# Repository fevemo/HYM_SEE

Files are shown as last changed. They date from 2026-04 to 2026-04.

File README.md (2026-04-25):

# Hack your microscope 2026 challenge - Group See

This repository contains all of the resources developed by group See for the HYM 2 day challenge: Organoid sorting with microfluidics.

The code provides visualization of the image caputred by a Hikrobotics camera with simultaneous control of the poseidon syringe pump system. On top of the real-time image we compute a difference image with respect to a reference and then identify flowing particles based on a tunable threshold level. Once the mask is computed the size of the particles is estimated by counting the total masked pixels.

## List of materials

-  [Poseidon pump system](https://github.com/pachterlab/poseidon)
-  [OpenUC2 Corebox](https://openuc2.com/product-overview-2/)
-  [Hikrobotics MV-CS060-10UM-PRO](https://www.hikrobotics.com/en/machinevision/productdetail/?id=5715)
-  [3x 1ml BD plastic syringe](https://www.digikey.pt/short/93zf92hf)
-  [2m of Tygon tube ND-100-80 (ID: 0.04 in, OD: 0.07 in)](https://darwin-microfluidics.com/products/tygon-nd-100-80-micro-tubing)
-  [3 Tube Tuck Luer Connector for 1/16 tubing (1 pack)](https://www.microfluidic-chipshop.com/connectors/1243-2683-tube-tuck-mini-luer-connector-for-116-tubing-fluidic-158-html#/20-material-tpe/26-color-blue)
-  [Custom open UC2 adapter plate for the XY stage](https://github.com/fevemo/HYM_SEE/blob/main/adapter_base_puzzle_v3.stl)
-  XY stage with M6 holes.
-  3x M6 screws
-  Slide holder made with Thorlabs parts: post-holder, optical post and two CL5 parts to clamp the microfluidic chip, using an M6 screw.
-  Windows PC.

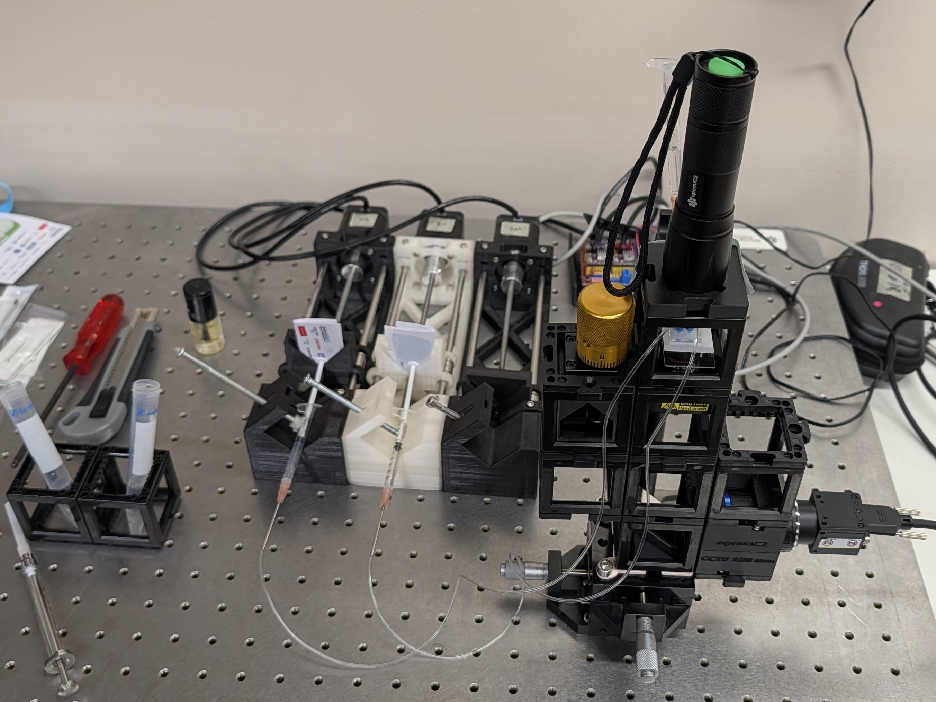
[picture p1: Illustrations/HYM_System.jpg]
HYM_System


## Optical setup
The microscope was build using the [OpenUC2 Corebox](https://openuc2.com/product-overview-2/). Documentation about the corebox can be found [here](https://docs.openuc2.com/usage/disc/corebox/en/core_intro/). The optical setup was adapted to be able to fit on a Melles Griot Stage for XY translation while fixing the sample with a Thorlabs post holder. An [adaptor](https://github.com/fevemo/HYM_SEE/blob/main/adapter_base_puzzle_v3.stl) was designed to fix the openUC2 microscope to the stage. 

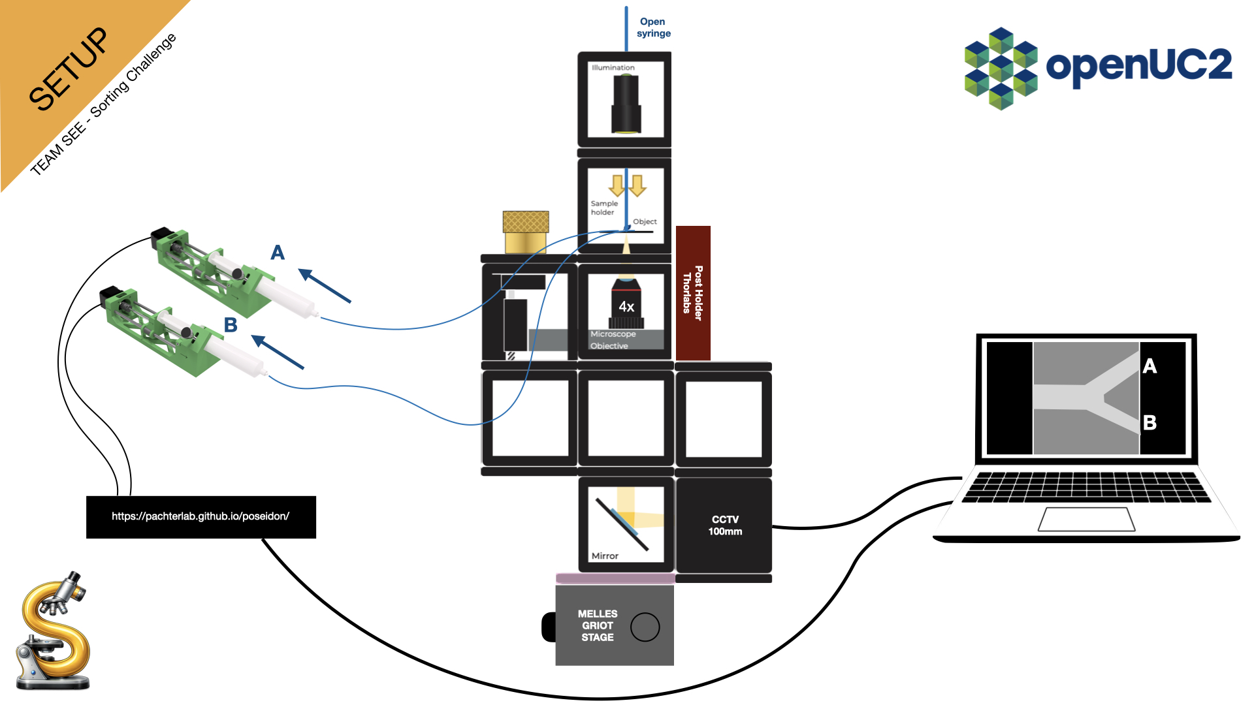
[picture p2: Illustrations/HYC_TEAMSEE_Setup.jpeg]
HYM_SEE_Setup


## Microfluidics design
The microfluidics [channel design](https://github.com/fevemo/HYM_SEE/blob/main/microfluidic-channel.stl) was lasercut into two layers of double sided tape, after which it was sticked on a glass microscopy slide. On top, a PMMA layer with in and outlets of 2.5mm (lasercut) was sticked on the top of the chip. ChipShop adaptors were inserted into the in and outlets to attach the tubing to the chip and connect them with the two syringe pumps. The inlet of the chip was connected with an open syringe in which the diluted particle sample can be loaded.

## Pump control
The Poseidon pumps were used in their original configuration and controled via serial commands from a custom python API. The API converts real-time control commands such as forward, back, stop, etc. into the command strings the Poseion arduino system expects. This was a great way to get up and running quickly but the serial comunication starts having issues as soon as several commands are sent in quick successsion. In the future it would be better to modify the pump controller to accomodate better real-time control.

## Camera control
The Hikrobot camera was controlled using the USB3 Vision protocol and using a custom API. Our API was built on an already existing API made available by Hikrobot (src/Python) and adapted for our specific use case. This API allows the connection to the camera, the start of acquisition, the change of exposure time, and the registering of a frame.

## Graphical User Interface
The GUI was made using napari as the main block. The camera and the syringe pumps were connected to the PC, and the communication was managed using Python. New frames were acquired in real time and used to update a napari layer, which enabled real-time visualization of the microfluidic chip. Some basic functions were implemented for camera control, such as the ability to change the exposure time of the camera and choose a folder in the PC for .tiff snap capture saving.

The ability to programmatically control the two syringe pumps was also implemented on the GUI, with speed control for each one and the ability to choose the pulling or pushing motion of the syringe, creating a forward or backward fluidic motion. Finally, a referencing button was also added, which could be used to create a subtraction image (subtraction_image = live - reference), which could be used for the segmentation of beads in the FOV.

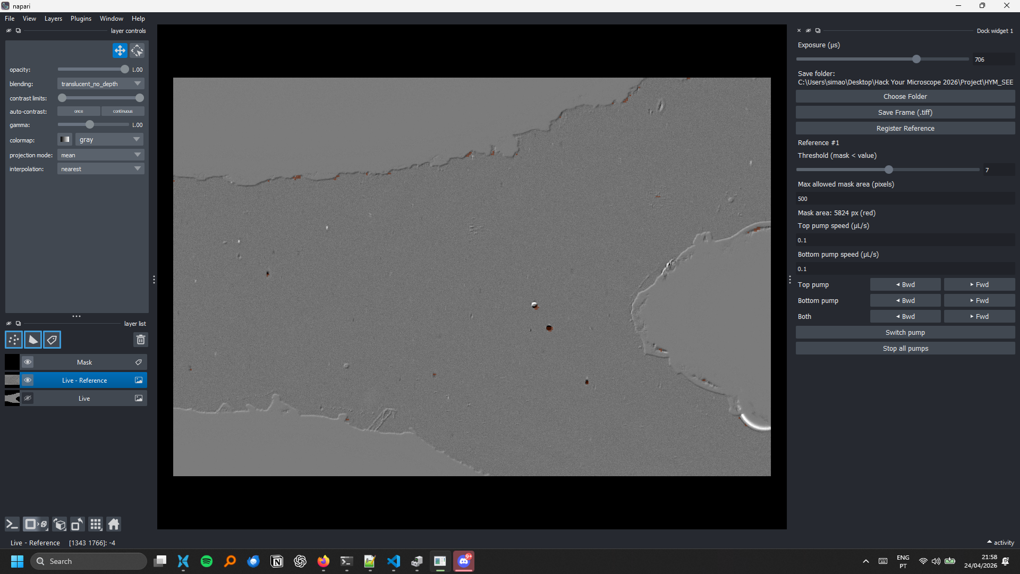
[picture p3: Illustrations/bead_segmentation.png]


## Setup

**macOS/Linux:**
```sh
./install.sh
source .venv/bin/activate
```

**Windows:**
```bat
install.bat
.venv\Scripts\activate
```

The install scripts will set up a Python 3.11 virtual environment and install all dependencies automatically.

**For camera control:**

Installation of the Hikrobotics MVS control software which includes the SDK installation.

## Run

Make sure the virtual environment is activated (see Setup above) before running. You need to do this each time you open a new terminal. Then run the desired code. 

```sh
python src/main_GUI.py
```

## Limitations / To-Dos:
1.	Software:
   
-	build on the already existing particle recognition and implement an automated feedback loop to the pumps to steer the particles to the correct outlet channel automatically.
  
2.	Hardware components:
 	
a.	Microfluidics:
-	Fine tuning of the pumps with adaptation of the pump’s response time for a more accurate sorting mechanism
-	Fine tuning of the microfluidic chamber width to optimise the response time to the pump system
-	The microfluid chip can be improved with a more optimised manufacturing process to achieve smoother edges.
-	a better inlet mechanism could be implemented to sort larger amounts of the sample.
  
b.	Optical Setup:
-	Implement a Fluorescence module for sorting based on spectral readout.

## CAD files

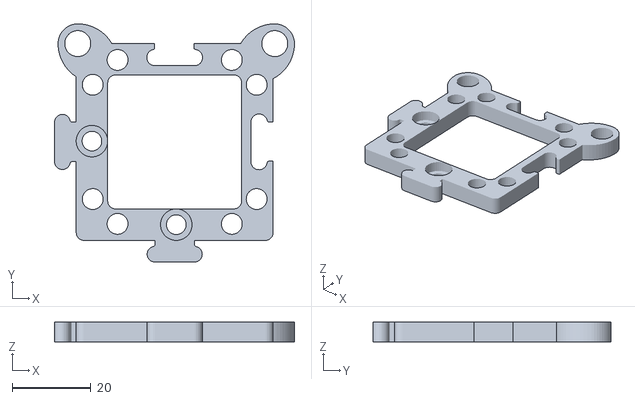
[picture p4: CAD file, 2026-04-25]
Hardware/adapter_base_puzzle_v3.stl
60.9 x 60.5 x 5.00

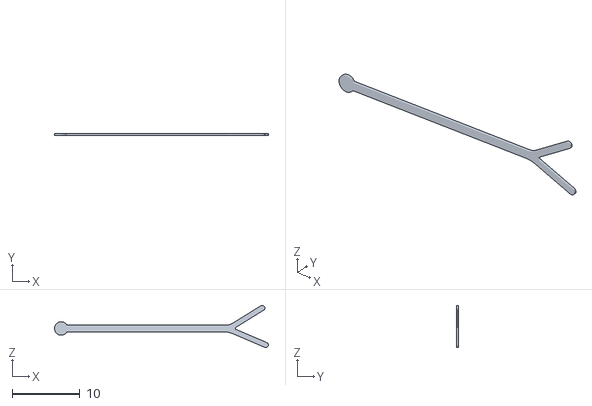
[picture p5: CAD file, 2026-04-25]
Hardware/microfluidic-channel.stl
31.6 x 0.3 x 6.24

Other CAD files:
Hardware/microfluidcs_channel_sketch.ipt

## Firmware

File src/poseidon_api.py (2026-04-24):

#!/usr/bin/env python3
"""
poseidon_api.py  -  Poseidon Pump serial API
=============================================

Two sending modes
-----------------
blocking=True  (default)
    Sends the command and waits for the Arduino's reply frame before returning.
    Use this for settings and for precise sequenced moves.

blocking=False  (fire-and-forget)
    Writes the bytes to the serial buffer and returns immediately without
    reading a reply.  Latency is essentially zero (just the USB write).
    Use this for start/stop automation where timing matters.

Quick start
-----------
    from poseidon_api import PoseidonController

    with PoseidonController("/dev/tty.usbmodem14101", microsteps=32) as pump:
        pump.set_speed(1, 1.0, "mL")
        pump.set_accel(1, 2.0, "mL")

        # ── fire-and-forget style (fast start / stop) ──
        pump.run_continuous(pumps=[1], direction="F", blocking=False)
        time.sleep(2.0)
        pump.stop(blocking=False)

        # ── blocking style (precise displacement) ──
        pump.move(1, 0.5, "mL", "F", blocking=True)
"""

import time
from threading import Lock
from typing import List, Optional

import serial
import serial.tools.list_ports

# ── Constants ─────────────────────────────────────────────────────────────────

BAUD_RATE = 230400

SYRINGE_OPTIONS = [
    "BD 1 mL", "BD 3 mL", "BD 5 mL",
    "BD 10 mL", "BD 20 mL", "BD 30 mL", "BD 60 mL",
]
SYRINGE_AREAS = [
    17.34206347, 57.88559215, 112.9089185,
    163.539454,  285.022957,  366.0961536, 554.0462538,
]  # mm² inner cross-section (BD plastic syringes)

# ── Conversion helpers ────────────────────────────────────────────────────────

def _mm2steps(mm: float, microsteps: int) -> float:
    """1 rev = 0.8 mm, 200 full steps/rev."""
    return mm / 0.8 * 200.0 * microsteps

def _to_steps(value: float, unit: str, area_mm2: float, microsteps: int) -> float:
    if unit == "mm":
        return _mm2steps(value, microsteps)
    if unit == "mL":
        return _mm2steps(value * 1000.0 / area_mm2, microsteps)
    if unit == "uL":
        return _mm2steps(value / area_mm2, microsteps)
    raise ValueError(f"Unknown unit '{unit}'. Use 'mm', 'mL', or 'µL'.")

# ── Serial low-level helpers ──────────────────────────────────────────────────

def _auto_port() -> Optional[str]:
    tokens = ["usbmodem", "usbserial", "wchusbserial", "ttyACM", "ttyUSB"]
    ports  = [p.device for p in serial.tools.list_ports.comports()]
    for tok in tokens:
        for p in ports:
            if tok.lower() in p.lower():
                return p
    return ports[0] if ports else None


def _read_frame(ser: serial.Serial, timeout_s: float = 2.0) -> Optional[str]:
    """Read one '<…>' reply frame from the Arduino."""
    deadline = time.time() + timeout_s
    while time.time() < deadline:
        b = ser.read(1)
        if b == b"<":
            break
    else:
        return None
    buf = bytearray()
    while time.time() < deadline:
        b = ser.read(1)
        if b == b">":
            return buf.decode("utf-8", errors="replace")
        buf.extend(b)
    return None


# ── Main API class ────────────────────────────────────────────────────────────

class PoseidonController:
    """
    Serial API for one Poseidon controller board (up to 3 pumps).

    Parameters
    ----------
    port        : Serial port string, or None to auto-detect.
    microsteps  : Microstepping level matching the physical driver jumper (1-32).
    syringe     : Syringe name from SYRINGE_OPTIONS (for mL/µL unit conversion).
    """

    def __init__(
        self,
        port: Optional[str] = None,
        microsteps: int = 32,
        syringe: str = "BD 1 mL",
    ):
        self._port       = port or _auto_port()
        self._microsteps = microsteps
        syringe_idx      = SYRINGE_OPTIONS.index(syringe)
        self._area       = SYRINGE_AREAS[syringe_idx]
        self._ser: Optional[serial.Serial] = None
        self._lock       = Lock()   # guards concurrent serial writes from threads

    # ── Context manager ───────────────────────────────────────────────────────

    def __enter__(self) -> "PoseidonController":
        self.connect()
        return self

    def __exit__(self, *_) -> None:
        self.disconnect()

    # ── Connection ────────────────────────────────────────────────────────────

    def connect(self) -> None:
        """Open the serial port and wait for the Arduino to boot."""
        print(f"[INFO] Connecting to {self._port} @ {BAUD_RATE} baud…")
        self._ser = serial.Serial(
            port=self._port, baudrate=BAUD_RATE, timeout=0.1
        )
        time.sleep(2.5)  # Arduino resets on serial open
        hello = _read_frame(self._ser, timeout_s=3.0)
        print(f"[INFO] Arduino: {hello or '(no greeting)'}")

    def disconnect(self) -> None:
        """Close the serial port."""
        if self._ser and self._ser.is_open:
            self._ser.close()
        self._ser = None
        print("[INFO] Disconnected.")

    @property
    def connected(self) -> bool:
        return self._ser is not None and self._ser.is_open

    # ── Raw send ──────────────────────────────────────────────────────────────

    def send_raw(self, cmd: str, blocking: bool = True) -> Optional[str]:
        """
        Send a raw '<…>' command string.

        Parameters
        ----------
        cmd      : Full command string including angle brackets.
        blocking : If True, wait for and return the Arduino reply frame.
                   If False, write and return immediately (fire-and-forget).

        Returns
        -------
        Reply string (blocking) or None (fire-and-forget / timeout).
        """
        if not self.connected:
            raise RuntimeError("Not connected. Call connect() first.")
        if not (cmd.startswith("<") and cmd.endswith(">")):
            raise ValueError(f"Command must be wrapped in <>: {cmd}")

        print(f"[TX] {cmd}")
        with self._lock:
            self._ser.write(cmd.encode("utf-8"))
            self._ser.flush()
            if not blocking:
                return None
            reply = _read_frame(self._ser, timeout_s=2.0)

        print(f"[RX] {reply or '(no reply)'}")
        return reply

    # ── Settings ──────────────────────────────────────────────────────────────

    def set_speed(self, pump: int, value: float, unit: str = "mm",
                  blocking: bool = True) -> Optional[str]:
        """Set speed for pump 1-3 in physical units per second."""
        steps = _to_steps(value, unit, self._area, self._microsteps)
        return self.send_raw(
            f"<SETTING,SPEED,{pump},{steps:.4f},F,0.0,0.0,0.0>", blocking
        )

    def set_accel(self, pump: int, value: float, unit: str = "mm",
                  blocking: bool = True) -> Optional[str]:
        """Set acceleration for pump 1-3 in physical units per second²."""
        steps = _to_steps(value, unit, self._area, self._microsteps)
        return self.send_raw(
            f"<SETTING,ACCEL,{pump},{steps:.4f},F,0.0,0.0,0.0>", blocking
        )

    # ── Motion: fixed displacement ────────────────────────────────────────────

    def move(self, pump: int, value: float, unit: str = "mm",
             direction: str = "F", blocking: bool = True) -> Optional[str]:
        """
        Move one pump by a fixed displacement and (optionally) wait for reply.

        The Arduino moves asynchronously once the command is received;
        'blocking' here only controls whether Python waits for the serial ACK,
        not for the motor to finish.
        """
        steps  = _to_steps(value, unit, self._area, self._microsteps)
        signed = steps if direction == "F" else -steps
        d      = [0.0, 0.0, 0.0]
        d[pump - 1] = signed
        return self.send_raw(
            f"<RUN,DIST,{pump},0.0,F,{d[0]},{d[1]},{d[2]}>", blocking
        )

    def move_all(self, values: List[float], unit: str = "mm",
                 direction: str = "F", blocking: bool = True) -> Optional[str]:
        """
        Move all 3 pumps simultaneously by given displacements.
        values = [v1, v2, v3]; use 0.0 to skip a pump.
        """
        d = [
            _to_steps(v, unit, self._area, self._microsteps)
            * (1 if direction == "F" else -1)
            for v in values
        ]
        return self.send_raw(
            f"<RUN,DIST,123,0.0,F,{d[0]},{d[1]},{d[2]}>", blocking
        )

    # ── Motion: continuous (run until stop) ───────────────────────────────────

    def run_continuous(
        self,
        pumps: List[int],
        direction: str = "F",
        blocking: bool = False,
    ) -> Optional[str]:
        """
        Start one or more pumps at their configured speed indefinitely.

        The firmware treats a distance of 999999 as "run until stopped",
        which is the same behaviour as the original RUN mode.

        Parameters
        ----------
        pumps     : List of pump IDs to run, e.g. [1], [1, 3], [1, 2, 3].
        direction : 'F' forward, 'B' backward.
        blocking  : False by default - returns immediately after writing
                    the command so you can time the stop precisely.
        """
        pump_str = "".join(str(p) for p in sorted(pumps))
        sign     = 1 if direction == "F" else -1
        dist     = sign * 999999.0
        # set distance for selected pumps only
        d = [dist if (i + 1) in pumps else 0.0 for i in range(3)]
        return self.send_raw(
            f"<RUN,DIST,{pump_str},0.0,F,{d[0]},{d[1]},{d[2]}>", blocking
        )

    # ── Stop ──────────────────────────────────────────────────────────────────

    def stop(self, blocking: bool = False) -> Optional[str]:
        """
        Stop all pumps immediately.

        blocking=False by default so the stop byte hits the Arduino as fast
        as possible - the OS serial buffer is flushed right away.
        """
        return self.send_raw("<STOP,BLAH,BLAH,BLAH,F,0.0,0.0,0.0>", blocking)

    # ── Convenience ───────────────────────────────────────────────────────────

    def wait(self, seconds: float) -> None:
        """Simple time-based wait between commands."""
        time.sleep(seconds)


# ── Smoke-test / example ──────────────────────────────────────────────────────

if __name__ == "__main__":
    with PoseidonController(microsteps=32, syringe="BD 1 mL") as pump:
        stop_delay = 1
        for pump_id in [1, 2]:
            pump.set_speed(pump_id, 1, "uL")
            pump.set_accel(pump_id, 10.0, "uL")

        for i in range(10):
            print("Both pumps")
            pump.run_continuous([1,2], direction="B", blocking=False)
            time.sleep(3)
            pump.stop(blocking=False)
            time.sleep(stop_delay)
            print("Pump 1")
            pump.run_continuous([1], direction="B", blocking=False)
            time.sleep(3)
            pump.stop(blocking=False)
            time.sleep(stop_delay)
            print("Pump 2")
            pump.run_continuous([2], direction="B", blocking=False)
            time.sleep(3)
            pump.stop(blocking=False)
            time.sleep(stop_delay)

        # print("\n── Blocking: precise 0.5 mL dispense ──")
        # pump.move(2, 0.5, "mL", "F", blocking=True)

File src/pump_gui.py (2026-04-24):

#!/usr/bin/env python3
"""
Poseidon Pump - Simple Jog GUI
==============================
Three pump columns with Forward / Backward buttons per pump.
Keyboard shortcuts:
  Pump 1 → Up / Down arrow keys
  Pump 2 → W / S keys
  Pump 3 → I / K keys

Usage:
    python pump_gui.py [--port /dev/tty.usbmodem14101]
"""

import argparse
import sys
import time
from typing import Optional

from PyQt5 import QtCore, QtGui, QtWidgets

from poseidon_api import (
    PoseidonController,
    SYRINGE_OPTIONS,
    SYRINGE_AREAS,
    _auto_port as _find_port,
    _to_steps as _displacement_to_steps_raw,
)

PUMP_COLORS     = ["#4A90D9", "#E67E22", "#27AE60"]
PUMP_LABELS     = ["Pump 1", "Pump 2", "Pump 3"]
UNIT_OPTIONS    = ["mm", "mL", "µL"]
MICROSTEP_OPTIONS = ["1", "2", "4", "8", "16", "32"]

KEY_BINDINGS = {
    0: (QtCore.Qt.Key_Up,  QtCore.Qt.Key_Down),
    1: (QtCore.Qt.Key_W,   QtCore.Qt.Key_S),
    2: (QtCore.Qt.Key_I,   QtCore.Qt.Key_K),
}


def _displacement_to_steps(value: float, unit: str, area_mm2: float, microsteps: int) -> float:
    return _displacement_to_steps_raw(value, unit, area_mm2, microsteps)


# ─────────────────────────────────────────────────────────────────────────────
# Worker thread - delegates to PoseidonController.send_raw (blocking)
# ─────────────────────────────────────────────────────────────────────────────

class CommandWorker(QtCore.QThread):
    reply = QtCore.pyqtSignal(str)

    def __init__(self, ctrl: PoseidonController, cmd: str, parent=None):
        super().__init__(parent)
        self._ctrl = ctrl
        self._cmd  = cmd

    def run(self):
        resp = self._ctrl.send_raw(self._cmd, blocking=True)
        self.reply.emit(resp or "(no reply)")


# ─────────────────────────────────────────────────────────────────────────────
# Main window
# ─────────────────────────────────────────────────────────────────────────────

class PumpWindow(QtWidgets.QMainWindow):
    def __init__(self, port: Optional[str], speed: float, accel: float):
        super().__init__()
        self._port  = port
        self._speed = speed
        self._accel = accel
        self._ctrl: Optional[PoseidonController] = None
        self._active_pump = 0
        self._workers: list = []
        self._command_in_flight = False

        # Per-pump state (index 0-2)
        self._pump_unit = ["mm", "mm", "mm"]
        self._pump_area = [SYRINGE_AREAS[0]] * 3   # default: BD 1 mL
        self._microstepping = 1

        self.setWindowTitle("Poseidon Pump Controller")
        self.setMinimumWidth(720)
        self._build_ui()
        self._apply_key_hint_labels()

    # ── UI construction ──────────────────────────────────────────────────────

    def _build_ui(self):
        root = QtWidgets.QWidget()
        self.setCentralWidget(root)
        vbox = QtWidgets.QVBoxLayout(root)
        vbox.setSpacing(12)
        vbox.setContentsMargins(16, 16, 16, 16)

        # ── Connection bar ──
        conn_row = QtWidgets.QHBoxLayout()
        self._port_combo = QtWidgets.QComboBox()
        self._refresh_ports()
        if self._port:
            idx = self._port_combo.findText(self._port)
            if idx >= 0:
                self._port_combo.setCurrentIndex(idx)

        self._connect_btn = QtWidgets.QPushButton("Connect")
        self._connect_btn.setFixedWidth(90)
        self._connect_btn.clicked.connect(self._toggle_connect)

        self._refresh_btn = QtWidgets.QPushButton("⟳")
        self._refresh_btn.setFixedWidth(36)
        self._refresh_btn.setToolTip("Refresh ports")
        self._refresh_btn.clicked.connect(self._refresh_ports)
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

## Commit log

2026-04-24 Added environment creation scripts and basic pump API + GUI
2026-04-24 Adding camera code
2026-04-24 Add pump GUI to napari
2026-04-24 Changed pump speed to only be applied when its modified
2026-04-24 AI slop fix for gui freezing after pump command
2026-04-24 Changed pump labels
2026-04-24 Added filtering and changed threshold limits
2026-04-25 Add files via upload
    This is the microfluidc channel layout, which was cut into two layers of double sided tape via laser cutter.
    [microfluidic-channel.stl]
2026-04-25 Add stl OpenUC2 adaptor
    [adapter_base_puzzle_v3.stl]
2026-04-25 Sketch design for microfluidic channel
    This is the sketch, which was used for the laser cutting process.
    [microfluidcs_channel_sketch.ipt]
2026-04-25 Incomplete list of materials
2026-04-25 List of materials updated
2026-04-25 Finished list of materials
2026-04-25 Update component list and descriptions in README
    Refined the list of required components and added details about the slide holder and XY stage.
2026-04-25 Details on pump control
2026-04-25 Clean up
    [adapter_base_puzzle_v3.stl, microfluidcs_channel_sketch.ipt, microfluidic-channel.stl]
